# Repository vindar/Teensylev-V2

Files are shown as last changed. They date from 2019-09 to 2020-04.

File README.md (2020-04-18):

# Teensylev-V2

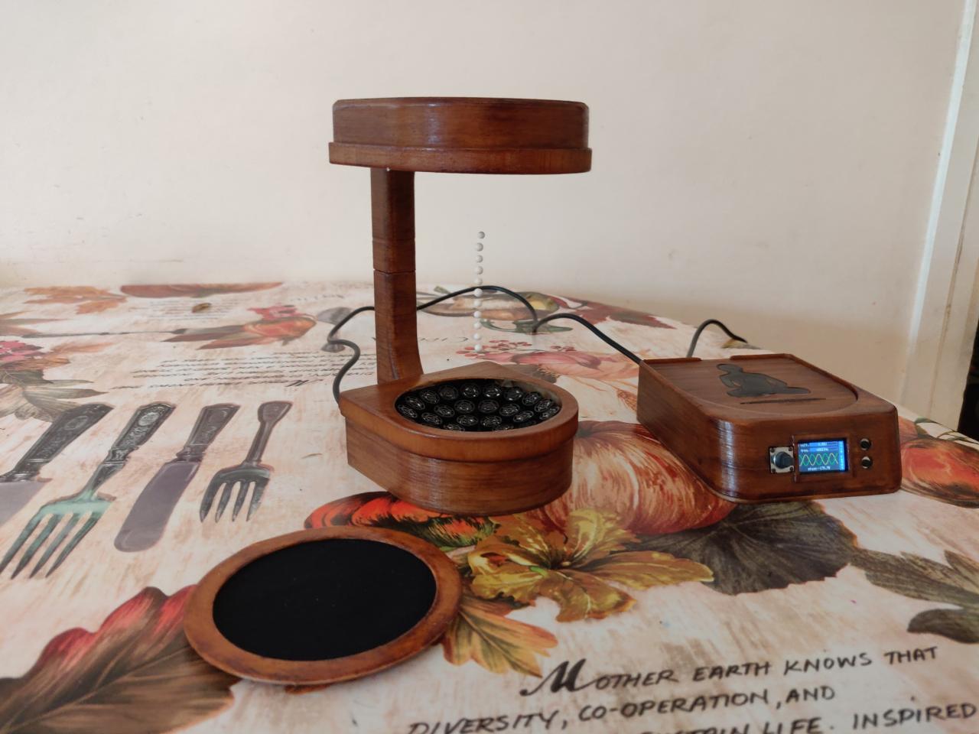
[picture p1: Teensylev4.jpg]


This repo contain the source code, STL files and schematics for a Teensy powered version of Asier Marzo's Tinylev acoustic levitator c.f. [Tinylev's Instructable](https://www.instructables.com/id/Acoustic-Levitator/)

**Build notes**

- 3D Printed in wood PLA. Stained and varnished. 

- Electronic assembly on a 90mm x 70mm perfboard (tight fit inside the control box, beware to leave some room at the front for the display). 

- Electronic components needed:  
   - 72 x Manorshi MSO-P1040-H07T transducers
   - Teensy 3.2 (mcu)
   - Pololu S18V20ALV (step up/step down, provides power to transducers) 
   - Pololu D24V10F5 (step up/step down to 5V, provides power to teensy) 
   - Pololu TB6612FNG (motor driver for driving the transducers)
   - Adafruit 3321. MiniTFT + Joystick (for control)
   - DC barrel jack (power connector)
   - 4 wires male/female connectors (for connecting the control box and the transducers arrays). 
   - misc: wires, 1/4W resistors, capacitors, 100K pot.

- Hack required to control the output voltage of S18V20ALV: a wire need to be soldered to the center leg of the mini pot. on the board. See [here](./Schematics/hack-S18V20ALV.png)

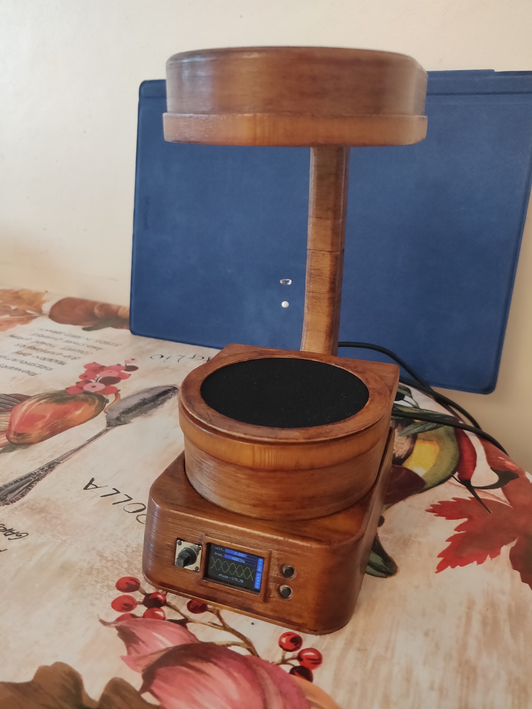
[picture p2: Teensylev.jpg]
Teensylev-V2


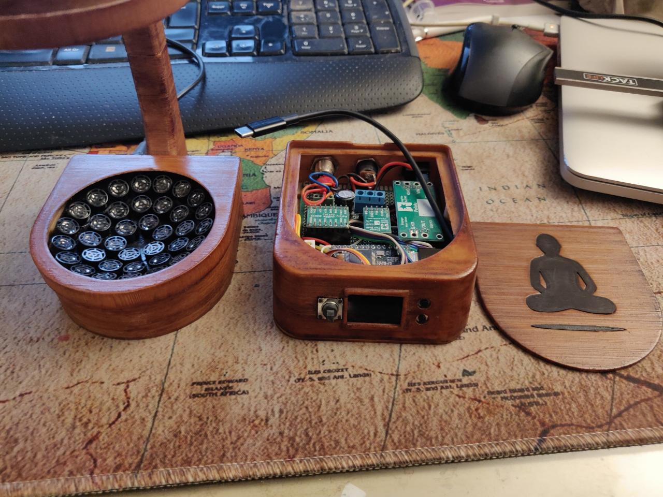
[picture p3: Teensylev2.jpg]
Teensylev-V2-2


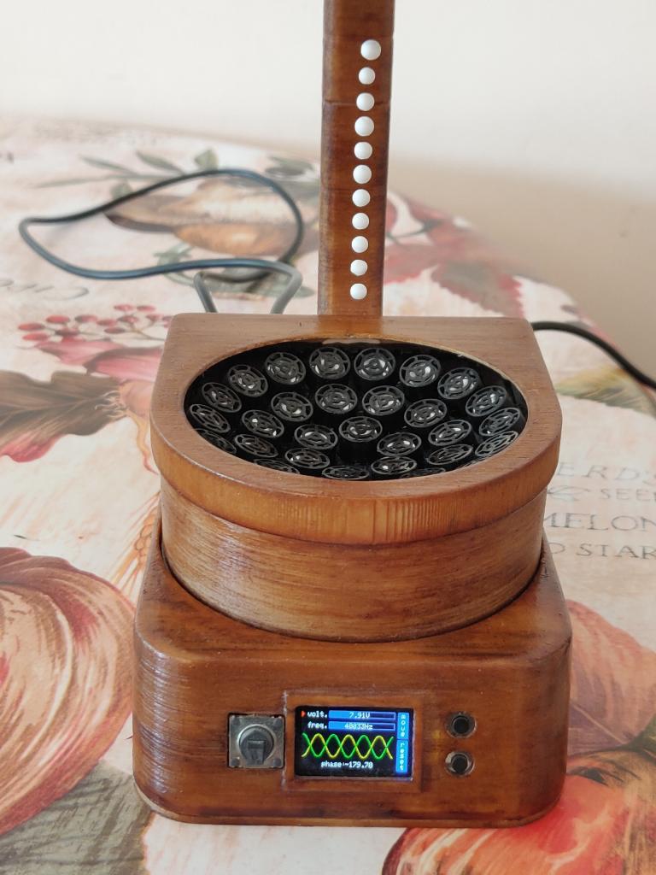
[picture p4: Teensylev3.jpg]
Teensylev-V2-3


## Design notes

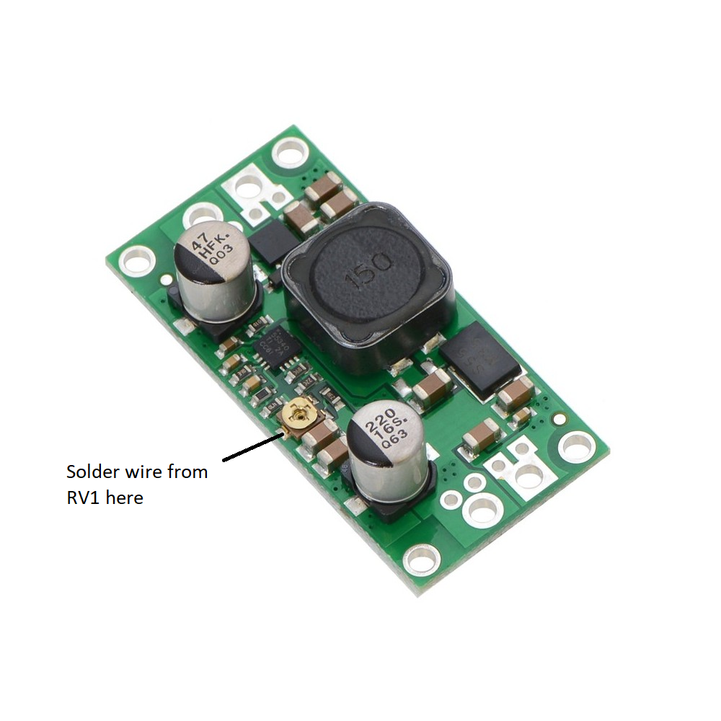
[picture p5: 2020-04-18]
Schematics/hack-S18V20ALV.png

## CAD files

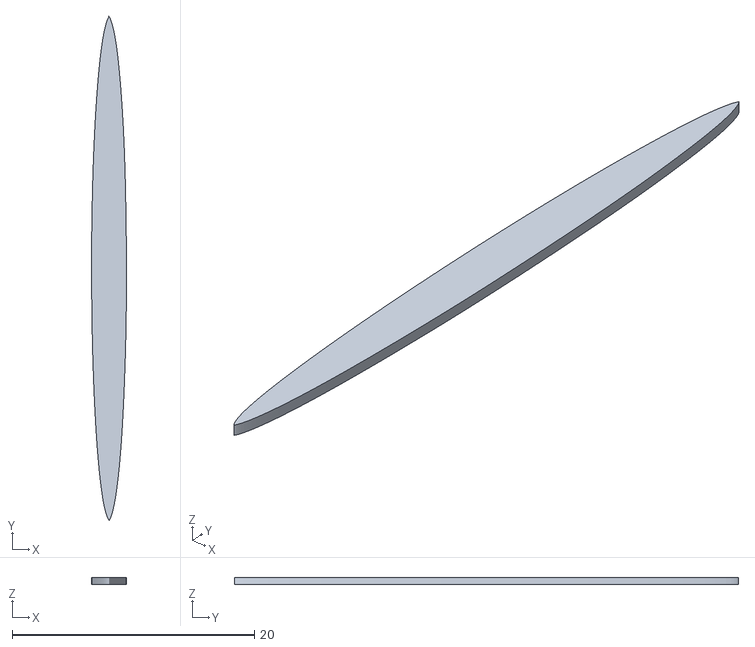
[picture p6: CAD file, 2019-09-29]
STLs/buddha_ellipse.stl
2.88 x 41.6 x 0.6

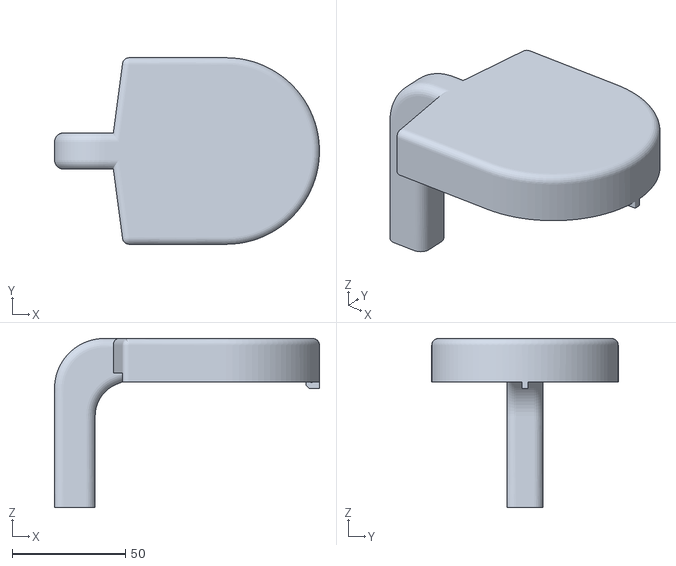
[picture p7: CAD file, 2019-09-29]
STLs/stand_top.stl
117.2 x 82.5 x 74.8

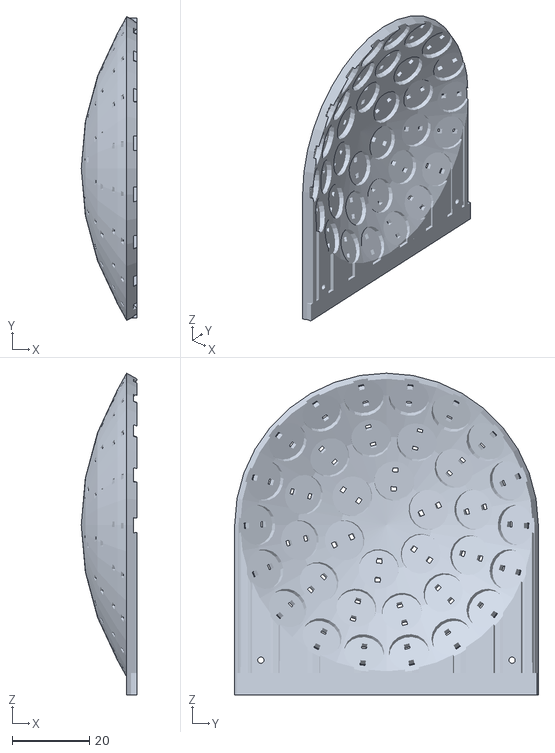
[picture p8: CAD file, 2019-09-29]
STLs/tinylev_splitted.stl
14.4 x 78.6 x 83.2

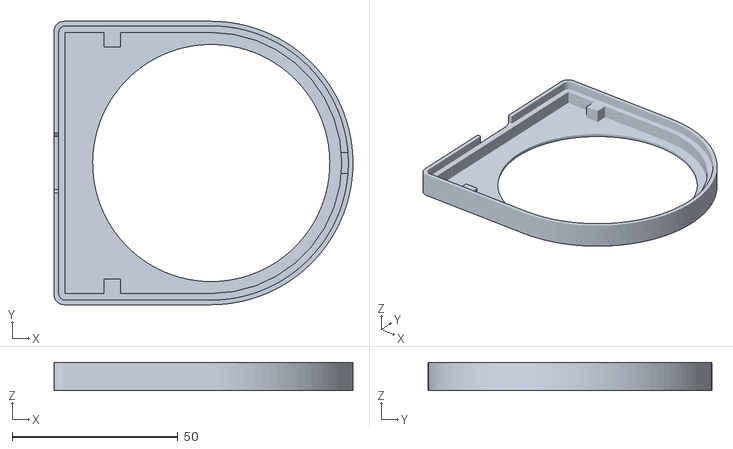
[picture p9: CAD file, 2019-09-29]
STLs/lid_top.stl
90.2 x 85.5 x 8.50

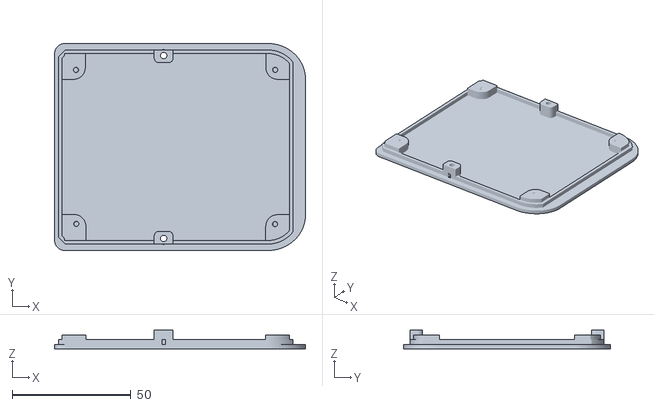
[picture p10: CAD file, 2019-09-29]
STLs/box_bottom.stl
105.8 x 87.3 x 7.80

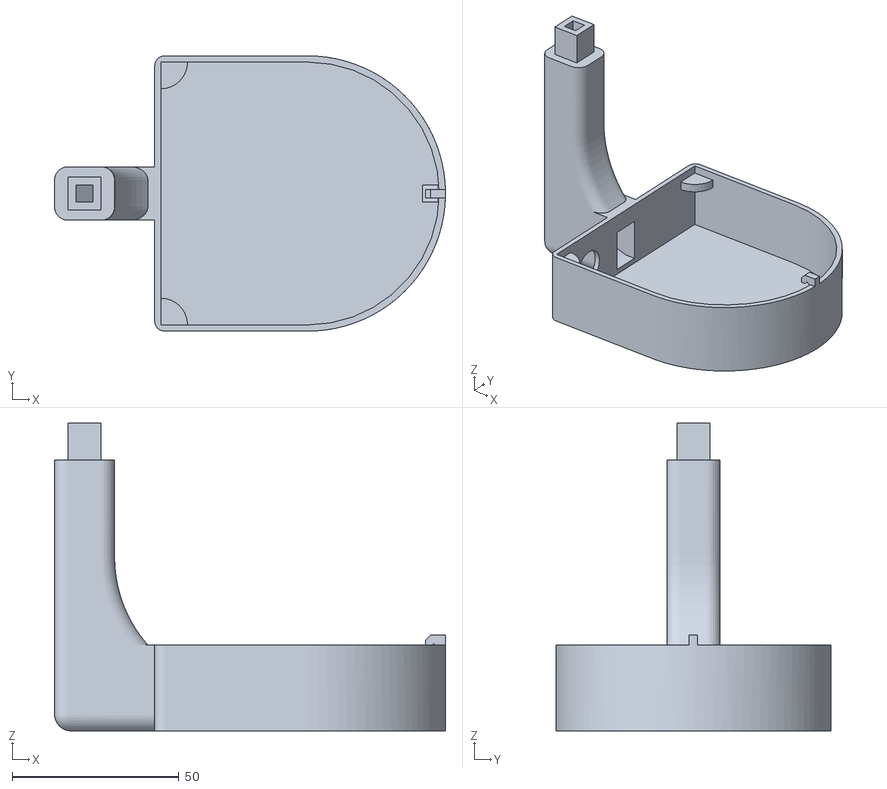
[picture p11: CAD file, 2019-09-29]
STLs/stand_bottom.stl
117.2 x 82.5 x 92.3

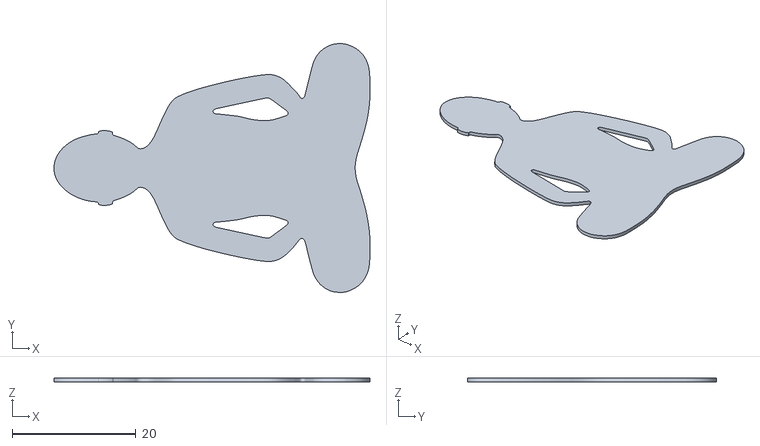
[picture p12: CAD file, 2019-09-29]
STLs/buddha_figure.stl
51.1 x 40.2 x 0.6

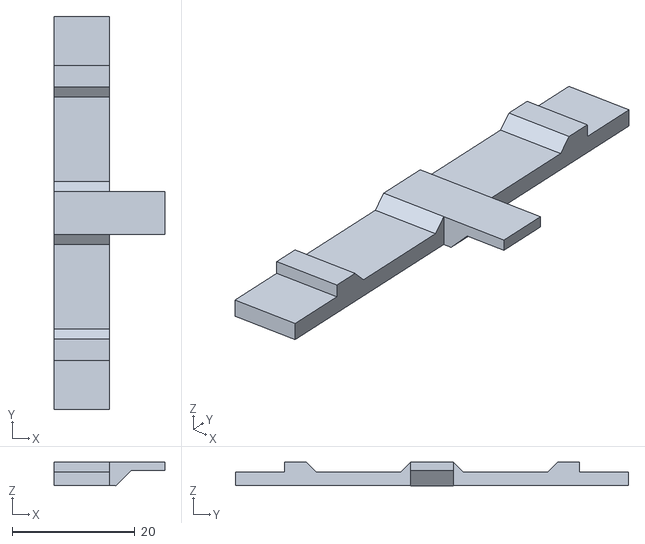
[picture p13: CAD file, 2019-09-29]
STLs/tft_holding_bar.stl
18.0 x 64.0 x 3.90

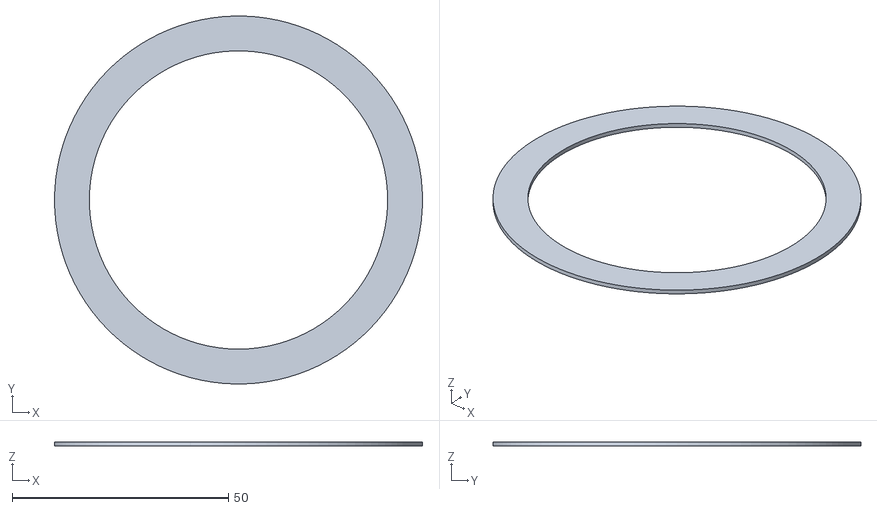
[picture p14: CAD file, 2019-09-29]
STLs/filter_part_2.stl
85.1 x 85.0 x 0.995

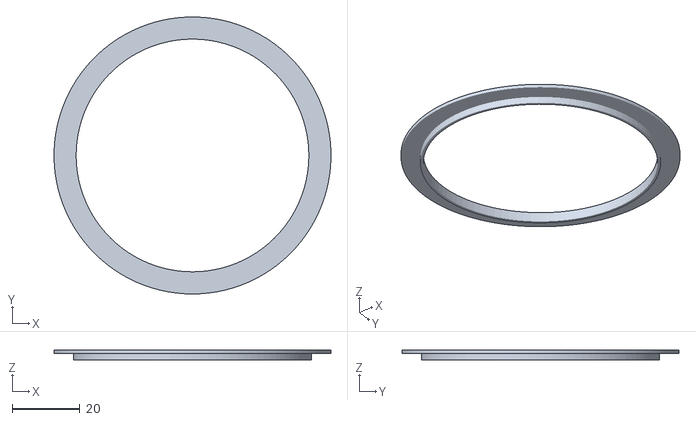
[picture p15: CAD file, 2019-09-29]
STLs/filter_part_1.stl
82.1 x 82.1 x 2.99

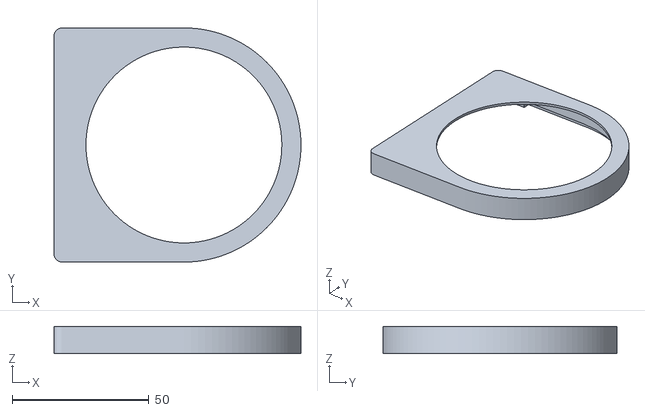
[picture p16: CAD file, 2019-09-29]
STLs/lid_bottom.stl
90.2 x 85.5 x 10.0

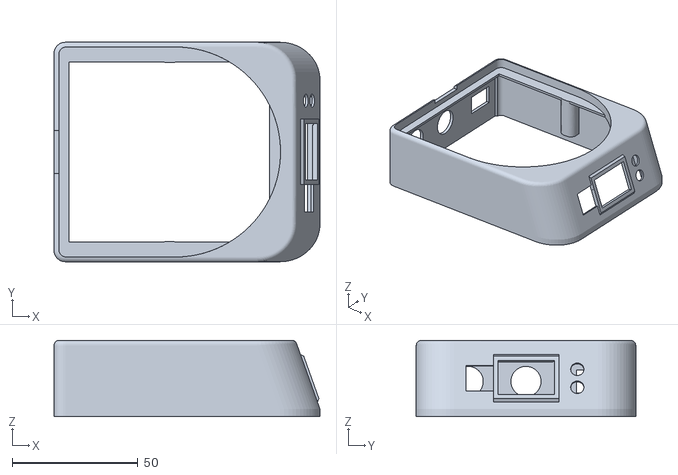
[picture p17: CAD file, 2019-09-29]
STLs/box_middle.stl
105.8 x 87.3 x 30.3

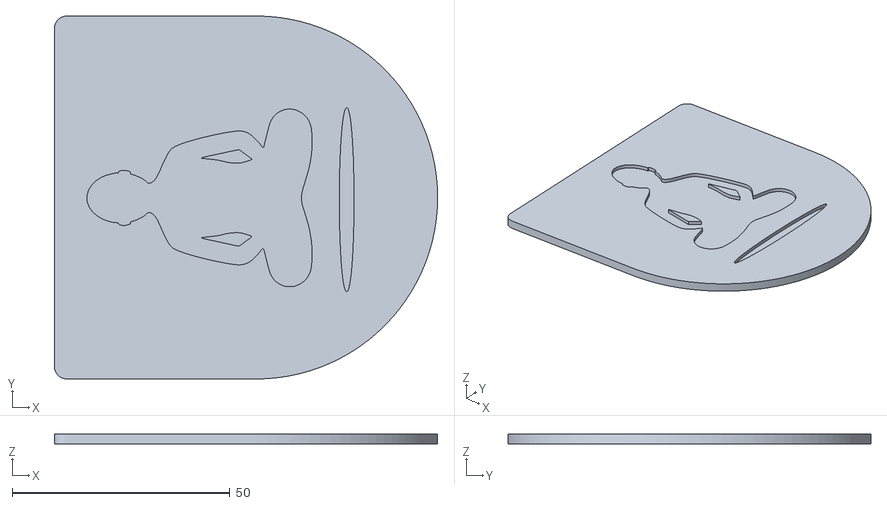
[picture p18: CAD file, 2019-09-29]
STLs/box_top.stl
88.0 x 83.3 x 2.40

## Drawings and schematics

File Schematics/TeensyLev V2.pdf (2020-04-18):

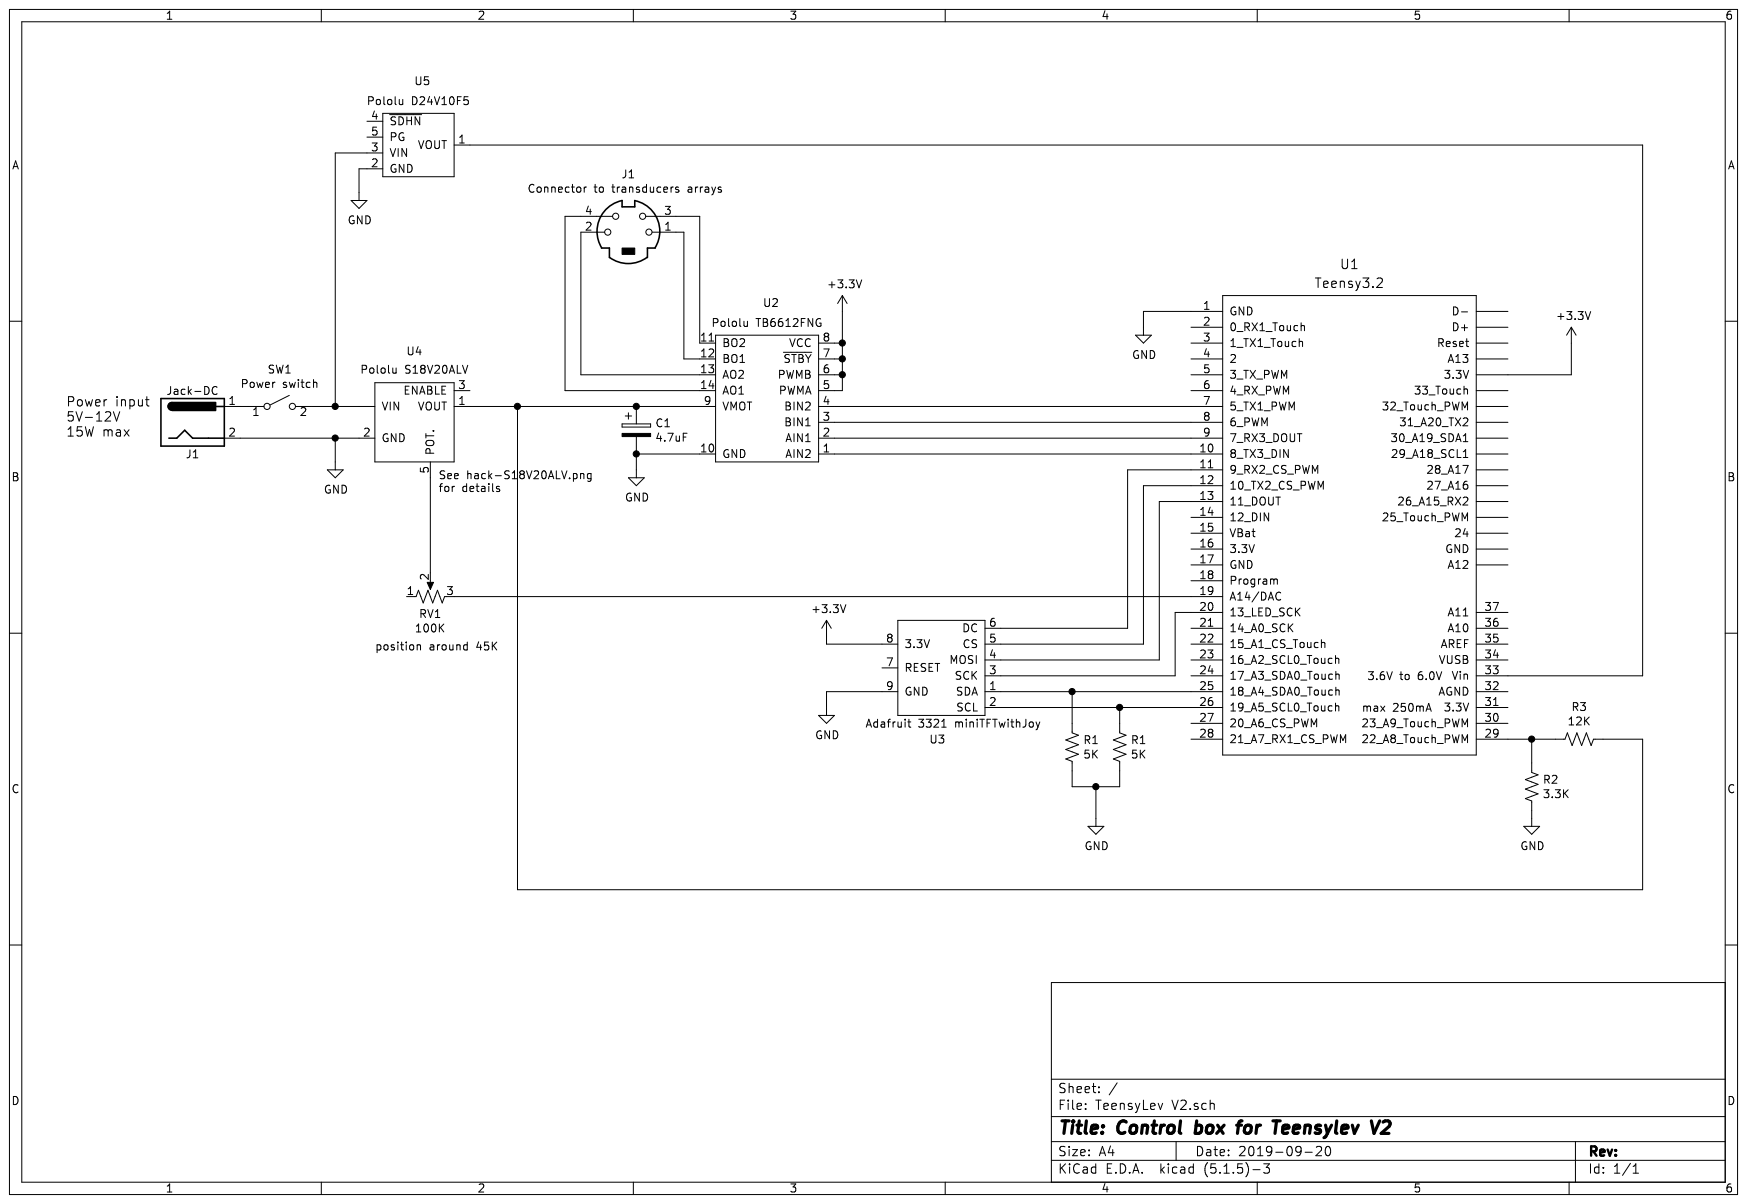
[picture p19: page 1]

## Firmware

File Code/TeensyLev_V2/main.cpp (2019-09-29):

/*
* main source file
* Created:  05/10/2018 23:07:43
* Author:   Vindar
*
* Source code for TeensyLev V2 (with adafruit mini TFT + joystick breakout).
*
*/


#include <Arduino.h>
#include <SPI.h>                            // spi library 
#include <DMAChannel.h>                     // DMA library by PJRC, use to generate stable 40Khz signal combined with FTM timers
#include <Adafruit_GFX.h>                   // Core graphics library -> USE THE ORIGINAL ADAFRUIT LIBRARY AND NOT THE OUTDATED TEENSY VERSION
#include <Adafruit_ST7735.h>                // Hardware-specific library for ST7735 -> USE THE ORIGINAL ADAFRUIT LIBRARY AND NOT THE OUTDATED TEENSY VERSION
#include <Adafruit_miniTFTWing.h>           // control button via seesaw
#include <Fonts/FreeSans9pt7b.h>            // font used
#include <Fonts/FreeMono12pt7b.h>           // font used

#include "fastcos.h"
#include "startlogo.h"





/**
* Very fast RNG. (for test purpose: no guarantee of good statistical properties). 
* The generator always use the same deterministic seed.
**/
class FastRNG
{

public:

    /* type of integer returned by the generator */
    typedef uint32_t result_type;

    /* Default constructor. Always initialize with the same seed. */
    FastRNG() : _gen_x(123456789), _gen_y(362436069), _gen_z(521288629) { }

    /* min value */
    static constexpr result_type min() { return 0; }

    /* max value */
    static constexpr result_type max() { return 4294967295UL; }

    /* return a random number */
    inline uint32_t operator()()
        {
        uint32_t t;
        _gen_x ^= _gen_x << 16; _gen_x ^= _gen_x >> 5; _gen_x ^= _gen_x << 1;
        t = _gen_x; _gen_x = _gen_y; _gen_y = _gen_z; _gen_z = t ^ _gen_x ^ _gen_y;
        return _gen_z;
        }

    /* return a uniform number on [0,1).  */
    inline float unif() { return ((float)(operator()())) / (4294967296.0); }

    /* discard results */
    void discard(unsigned long long z) { for (unsigned long long i = 0; i < z; i++) operator()(); }


private:

    uint32_t _gen_x, _gen_y, _gen_z;        // state of the generator

};



/* generate N(0,1) random variable using "ratio of uniform" method 
   taken from "Numerical recipies in C++" 
 */
template<class random_t> inline float normalLaw(random_t & gen)
    {
    float u, v, x, y, q;
    do {
        u = gen.unif(); v = 1.7156*(gen.unif() - 0.5);
        x = u - 0.449871; y = abs(v) + 0.386595;
        q = (x*x) + y * (0.19600*y - 0.25472*x);
        } 
    while ((q > 0.27597) && (q > 0.27846 || (v*v) > -4.*logf(u)*(u*u)));
    return (v / u);
    }


/**********************************************************************
* MISC
**********************************************************************/


/** Format a floating point value inside a buffer */
char * tostring(char * dest, float val, const char * unit) { sprintf(dest, "%.2f%s", val, unit); return dest; }

/** Format an integer value inside a buffer */
char * tostring(char * dest, int32_t val, const char * unit) { sprintf(dest, "%li%s", val, unit); return dest; }



/**********************************************************************
* VOLTAGE CONTROL
**********************************************************************/

const int32_t ANALOG_RES_BIT = 10;                                  // DO NOT CHANGE -> does not work with other values
const int32_t ANALOG_RES = (((int32_t)1) << ANALOG_RES_BIT) - 1;    // 

const int VOLTAGE_SENSOR_PIN = A8;                                  // analog pin to detect current voltage. 
const int VOLTAGE_CONTROL_PIN = A14;                                // DAC pin to adjust voltage

const float DEFAULT_DAC = 0.5;                                      // default start value
const float DAC_STEP = 0.005;                                       // change step

volatile float _dac = DEFAULT_DAC;                                  // current dac value


volatile float prev_voltage = 0;
                                                                    /* return the current voltage */
inline float voltage()
{
    int32_t r = analogRead(VOLTAGE_SENSOR_PIN);
    float v = ((r*3.3f) / ANALOG_RES) * ((3.3 + 12.0) / 3.3); // voltage divider with resistors of 3.3K and 12K
    const float diff = v - prev_voltage;
    if ((diff <= 0.02) && (diff >= -0.02))
        {
        v = prev_voltage;
        }
    prev_voltage = v;
    return v;
}

/* return the current dac value between 0.0 and 1.0 */
inline float getDAC() { return _dac; }

/* set the dac value between 0.0 and 1.0 */
inline void setDAC(float val = DEFAULT_DAC)
{
    if (val < 0.0f) val = 0.0f; else if (val > 1.0f) val = 1.0f;
    _dac = val;
    int32_t V = (int32_t)((1.0f - _dac)*ANALOG_RES);
    analogWrite(VOLTAGE_CONTROL_PIN, V);
}

/* increase dac */
inline void incDAC() { setDAC(_dac + DAC_STEP); }

/* decrease dac */
inline void decDAC() { setDAC(_dac - DAC_STEP); }

/* initialization */
void initVoltage()
{
    analogReference(EXTERNAL);
    analogReadAveraging(32);
    analogWriteResolution(ANALOG_RES_BIT);
    analogReadResolution(ANALOG_RES_BIT);
    pinMode(VOLTAGE_SENSOR_PIN, INPUT);     // pin for reading voltage
    pinMode(VOLTAGE_CONTROL_PIN, OUTPUT);   // pin  for setting voltage
    setDAC();                               // set the default voltage
}


/**********************************************************************
* FTM TIMERS
**********************************************************************/


/* convert mod to frequency */
constexpr int32_t freq_to_mod(double freq) { return (int32_t)(F_BUS + freq) / (2 * freq); }

/* convert frequency to mod */
constexpr double mod_to_freq(int32_t mod) { return ((double)F_BUS) / (2 * mod - 1); }


const double DEFAULT_FREQ = 40000;
const double MIN_FREQ = 5000;
const double MAX_FREQ = 80000;

const int32_t DEFAULT_MOD   = freq_to_mod(DEFAULT_FREQ);        // mod for default frequency
const int32_t MIN_MOD       = freq_to_mod(MIN_FREQ);            // mod for min frequency
const int32_t MAX_MOD       = freq_to_mod(MAX_FREQ);            // mod for max frequency

volatile int32_t _mod;      // number of ticks per period w.r.t the internal clock to get frequency freq.
volatile int32_t _phase0;   // position of the first trigger; must be between 1 and mod -1
volatile int32_t _phase1;   // position of the second trigger; must be between 1 and mod -1
volatile int32_t _diff;     // keep track of the two pi phase difference


/* return the current frequency */
inline double getFreq() { return mod_to_freq(_mod); }

/* create and start the timer */
inline void createTimer()
{
    _mod = freq_to_mod(DEFAULT_FREQ);                           // set number of ticks w.r.t. frequency
    _phase0 = _mod / 2;                                         // first trigger
    _phase1 = _mod / 2 + 1;                                     // second trigger
    _diff = 0;                                                  // no phase diff
                                                                // set the FTM timer    
    FTM2_SC = 0;                                                // status and control initially disabled
    FTM2_CNT = 0;                                               // set counter at zero
    FTM2_MOD = _mod - 1;                                        // store it
    FTM2_SC = FTM_SC_CLKS(1) | FTM_SC_PS(0);                    // start the timer using the system clock. (divide by 1)
    FTM2_C0SC = 0x69;                                           // channel interrupt enable and edge aligned pwm
    FTM2_C1SC = 0x69;                                           // channel interrupt enable and edge aligned pwm
    FTM2_C0V = _phase0;                                         // trigger CH0 at this value -> must not be 0 or mod-1
    FTM2_C1V = _phase1;                                         // trigger CH1 at this value -> must not be 0 or mod-1
    CORE_PIN32_CONFIG = PORT_PCR_IRQC(1) | PORT_PCR_MUX(3);     // pin 32 is associated with FTM2_CH0 (mux(3)  and triggers DMA(port B) on rising edge (IRQC(1))    
}


/** Increment phase */
inline void incPhase()
{
    _diff++;
    if (_diff >= _mod - 1) _diff = -_mod + 1;
    if (_phase0 < _mod - 1) { FTM2_C0V = (++_phase0); return; }
    FTM2_C0V = _phase0 = 1;
    return;
}


/** Decrement phase */
inline void decPhase()
{
    _diff--;
    if (_diff <= -_mod) _diff = _mod - 2;
    if (_phase1 < _mod - 1) { FTM2_C1V = (++_phase1); return; }
    FTM2_C1V = _phase1 = 1;
    return;
}


/** return the phase difference in [-1,1] */
inline float getdiffphase()
{
    return (-1.0f + 2 * ((float)(_diff + _mod - 1)) / ((float)(2 * _mod - 2)));
}
    



/**********************************************************************
* PHASE AND FREQUENCY CONTROL VIA INTERRUPT
**********************************************************************/

const int8_t            UP   = 1;   // phase directions
const int8_t            DOWN = -1;  // 
const int8_t            NONE = 0;   // 

const int32_t DEFAULT_COMMAND_RATE = 1000;  // 1ms between counts


/** Structure containing a phase command, chained list */
struct PhaseCommand
    {
    PhaseCommand * next;        // pointer to the next command (or nullptr if no more command)
    int32_t rate;               // number of microsecond between each count
    int32_t count;              // number of counts to perform (negative = infinite)
    int8_t  dir;                // direction of the phase shifting (UP or DOWN or NONE)
    };


IntervalTimer       phaseint;       // object that manage the interrupt routine

/* command being executed */
volatile int32_t        current_count;      // number of count remaining
volatile int32_t        current_rate;       // current interrupt rate
volatile float          current_mult_scale; // current mult scale factor
volatile int8_t         current_dir;        // direction of the current command
volatile PhaseCommand * current_com;        // pointer to the command structure

const int32_t DELTA_MINMAXPOS = 500;

volatile int32_t        current_position;       // current position
volatile int32_t        min_position;           // min position
volatile int32_t        max_position;           // min position

/* command modifier */
volatile float          adjust_mult_scale = 1.0f;   // scale multiplier
volatile float          adjust_rate_scale = 1.0f;   // rate multiplier
volatile int32_t        adjust_offset = 0;          // offset to apply

const int32_t MAX_ADJUST_OFFSET_RATE = 1000;    // rates bound 
const int32_t MIN_ADJUST_OFFSET_RATE = 200;     // for offset change

const int32_t OFFSET_UNIT = 1000;   // INCEMENT/DECREMENT VALUE FOR OFFSET
const float MULT_RATE_UNIT = 1.1;   // INCREMENT/DECREMENT VALUE FOR COMMAND COUNT RATE MULTIPLIER
const float MULT_SCALE_UNIT = 1.1;  // INCREMENT/DECREMENT VALUE FOR COMMAND COUNT SCALE MULTIPLIER
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
